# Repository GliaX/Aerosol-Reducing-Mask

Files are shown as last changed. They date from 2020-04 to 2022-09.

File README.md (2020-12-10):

November 27, 2020

# Suspension of Marketing and Sales of the Aerosol-Reducing-Mask (ARM)

Effective November 27 (2020), the ARM team is suspending any sales or distribution of the current version of the ARM.

Review of clinical trial data that became available to the team on November 26  shows that the ARM device is not as effective at reducing leak and aerosolization as earlier data had suggested. The [preliminary data and analysis report](https://github.com/GliaX/Aerosol-Reducing-Mask/blob/master/reports/20201210%20Clinical%20Trial%20Summary%20Leak%20Data.md) is posted to the repository.

The clinical trial was not a requirement for regulatory approval from Health Canada and the device is still approved under an Interim Order. However the trial data suggests that while safe and effective at providing respiratory support, the device fails to meets its primary indication (protection of health care providers and other patients from infectious aerosols), we are withholding all sales and deployments of the device.

We are currently undertaking a detailed analysis of the device and causes of failure in order to create a road map for required modifications for a subsequent version. Such modifications and the necessary testing will likely not be completed in sufficient time to meet current urgent needs. All analysis reports and other documents will continue to be posted on the public repository.

# Aerosol Reducing Mask for Non-Invasive Ventilation

## Purpose
The Minimizing Aerosolization In Non-invasive (MAIN) Ventilation COVID-19 mask
is a sealed, filtered, full-face mask minimizing virus aerosolization and
enabling the use of Non-Invasive Positive Pressure Ventilation (NIPPV) machines
for patients with COVID-19, or similar symptoms.  The mask adaptor is the
primary connection between the sealed facemask and standard medical 22mm
respiratory tubing, fittings and filters. An additive manufacturing method, also
known as 3D printing, was used to produce the mask adapter because of its
relative speed to make objects of complicated geometries and availability. Due
to the medical nature of the adapter, certain specifications must be followed in
its production to prevent any infectious transmission from the patient to health
care workers and other patients.

## Bill Of Materials
 * [3M Scott AV-2000 Facepiece](https://www.3mscott.com/products/av-2000-facepiece/)
 * 3M Gasket seal
 * 3D printed adapter (ABS)
 * Safety release strap, 25mm width x 35cm length[[MEC](https://www.mec.ca/en/product/5020-829/1%22%2825mm%29-Nylon-Tubular-Climbing-Webbing)]

## Adaptor 3D Printing Specifications and Parameters

 * Adapter Version: v1.0
 * Filament Material: ABS
 * Printer Nozzle: 0.4mm
 * Infill Percentage & Pattern: 100% Infill, Rectilinear infill
 * Wall thickness: 2.0mm (5 wall/perimeters with 0.4mm nozzle)
 * Top and bottom thickness: 2.0mm (5 top and bottom layers at 0.2mm layer height)
 * Supports: Required
 * Raft: Not preferred; Printing on the bed creates a smoother finish
 * Orientation: Mask face on the bed, Outer face upwards (See Figure 1)

Additional Slicer Settings:
 * Use ‘random start points for all perimeters’ (Cura)
 * Use ‘Connect infill lines’ (Cura)
 * Use ‘Random start points for all perimeters’ (Simply3D)

Figure 1: Orientation of Adapter v1.0 on Print Bed

*Figure 1: Orientation of Adapter v1.0 on Print Bed*

* NOTE: ABS is prone to thermoplastic contraction (shrinkage). If the slicing
software does not already compensate for this shrinkage, consider measuring the
product to ensure the correct scale. Amount of contraction can vary between
different brands of ABS – printing calibration tools and test-prints recommended
to determine exact percentage to scale.

## Post-Print Check Guidelines
Ensure the following:
 * Inside diameter of female port on outward face should measure between 22.37
 +0.1/-0.15mm on outside face (see Figure 2). Use of digital calipers strongly
 recommended.
 * Note tolerances for other dimensions post printing (also see Figure 2).
 * Layers adhere properly to each other
 * Walls are completely fused together
 * Surfaces (outer and inner) are smooth without gaps, burrs, blobs
 * The print has decent flexibility (i.e. latch)

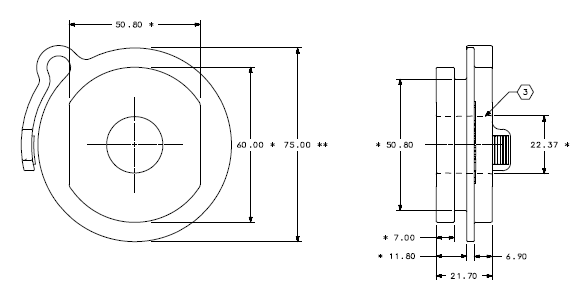
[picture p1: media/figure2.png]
Figure 2: Critical part dimensions


*Figure 2: Critical part dimensions*

# Print Traceability Guidelines

For each batch printed, the following items must be logged:
 * Material used
 * Lot number of material used
 * Colour of material
 * Date of print
 * Machines used for print
 
# Attaching safety release
 
 * Insert strap into bottom right buckle of helmet - Patient should be able to pull strap with right hand.
 * Loop strap back approximately 6 cm.
 * Sew firmly using 3 runs across the area to sew.
 
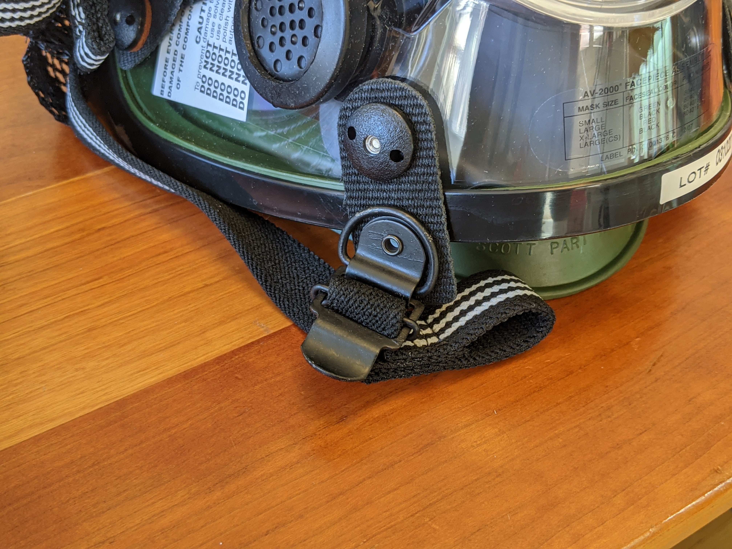
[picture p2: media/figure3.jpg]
Figure 3: Front view of helmet

 
*Figure 3: Front view of helmet*
 
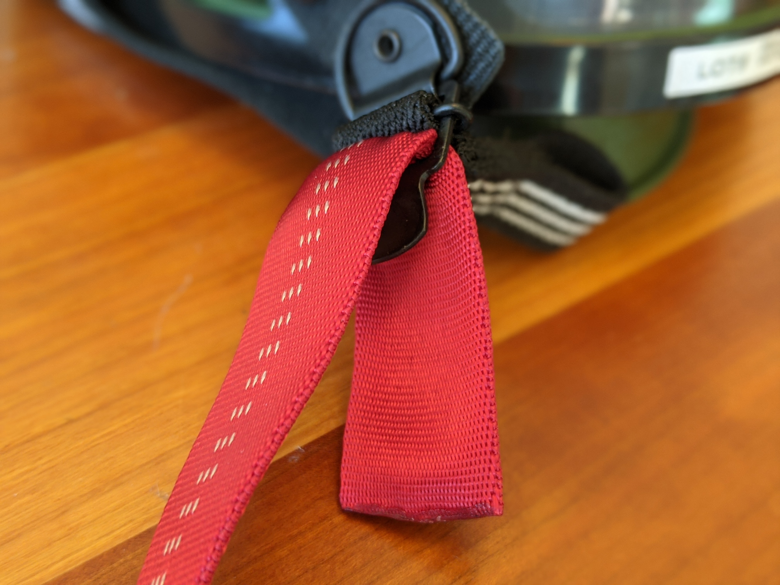
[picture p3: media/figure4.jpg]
Figure 4: Strap inserted into buckle


*Figure 4: Strap inserted into buckle*

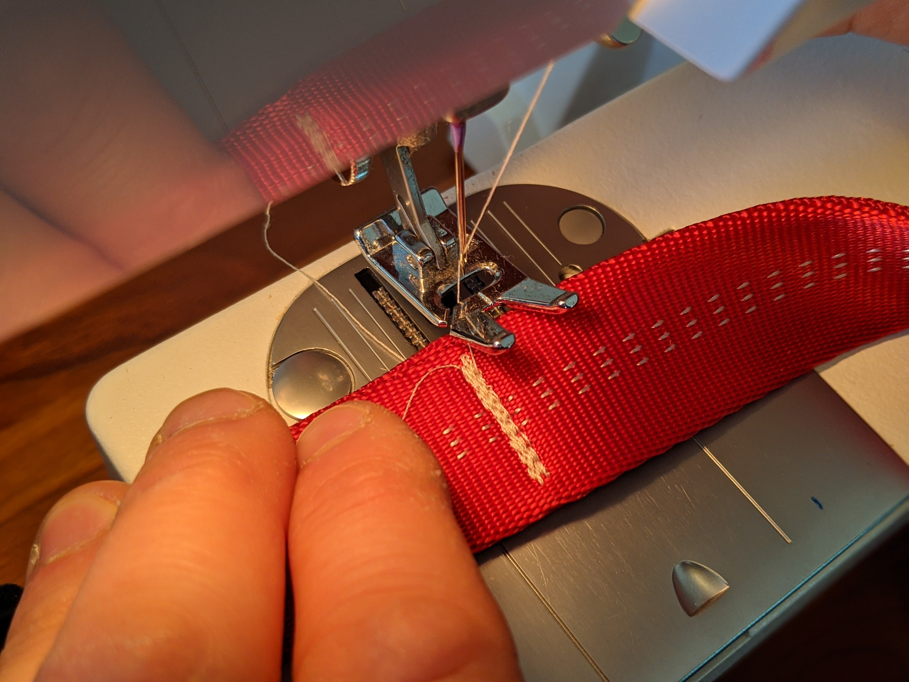
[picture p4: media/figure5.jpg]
Figure 5: Completed sewn strap

 
*Figure 5: Completed sewn strap*

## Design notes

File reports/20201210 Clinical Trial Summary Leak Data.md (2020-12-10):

---
tags: Glia-ARM
---
# Glia-ARM Clinical Trial Summary Report of Leak Data

Source: https://hackmd.io/@ARM/HyMZ32JnP

## Objective
To evaluate the effective leakage of the ARM compared to current standard of care NIV masks in patients undergoing emergent CPAP or BiPAP treatment.

## Methods
<small>The study was an opportunistic randomized controlled trial.

After [HSREB approval at Western University](https://github.com/GliaX/Aerosol-Reducing-Mask/blob/master/ethics_application/2020-04-27%20Ethics%20Approval.pdf) participants determined to require non-invasive ventilation by attending MDs in the emergency departments of affiliated teaching hospitals were recruited and randomized to the ARM or control standard mask ([Fisher & Paykel RT043M non-vented mask with anti-asphyxiation valve](https://www.fphcare.com/en-ca/hospital/adult-respiratory/noninvasive-ventilation/rt043/)).

Patients requiring NIV for an actue indications were assessed for inclusion. Exclusion criteria were: Age $\lt$ 18 years; respiratory failure due to non-pulmonary pathology; impaired level of consciousness (Glasgow coma scale $\lt$ 10); upper gastrointestinal bleeding; Chest trauma; Agitatation or violence.

Patients were ventialted using a Resmed (San Diego, US) Stellar 150 Non-invasive ventilator. The device's internal leak logging system was used to document mask leak. Trial was continued until either NIV was no longer deemed medically indicated by the attending team to a maximum of 24 hours. Arterial or venous blood gases collected during routine care of the patient were monitored to ensure adequacy of ventilation.

Primary end-point was proportion of time under treatment with mask leak $\lt$ 0.5 L/min (registering as 0 L/min by machine). Secondary end-points included ulceration score (National Advisory Panel on Pressure Ulcer Scale), mask fit (Likert-like 5 point scale, 1 = poor; 5 = excellent); and patient tolerance of the device (1 = poor; 5 = excellent).

Additional collected data included: demographics (age, sex); morphologic parameters (height, weight, presence of dentures, facial hair); metabolic data (arterial or venous blood gas); vital signs (temperature, pulse, respirations, blood pressure, oxygen saturation); Ventilation parameters (mode, IPAP, EPAP) and fit and comfort (mask fit evaluated by RT, and patient tolerance of mask).

</small>

## Results
The study was stopped after randomization of 16 patient (6 intervention, 10 control) due to results suggesting failure of the ARM to reduce leaks compared to the control device (Fig T1 & T2).

There were no major adverse events during the trial related to the device. 

T1. Mask Leak - Control

***Fig T1**. Distribution of mask leak flows for each patient with the control mask (N=10). 7/10 patients had leak of 0.5 L/min or less for at least half of the treatment duration*

T2. Mask Leak - ARM

***Fig T2**. Distribution of mask leak flows or each patient with the ARM (N=6). Only 2 of 6 patients had leaks of 0.5 L/min or less for more than half of the treatment duration*.

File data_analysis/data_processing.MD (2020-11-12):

* Download and compile [EDF2ASCII](https://www.teuniz.net/edf2ascii/)
* Get data from patient
* Start time is found in 

```
for f in `ls *BBB.edf`; do ~/workspace/EDF/edf2ascii $f; cat ${f%%.*}_annotations.txt | grep -i leak > ${f%%.*}_leak.txt; sed -i 's/,Leak://g' ${f%%.*}_leak.txt ; done

```

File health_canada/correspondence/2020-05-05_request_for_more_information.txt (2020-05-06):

Dear Dorotea and Dr. Loubani:

This pertains to the interim order application for the above device.  We require the following information to complete our assessment: 

1)     Since some components are 3D printed, provide biocompatibility testing results for any identified risks as per ISO 18562-1 and 10993-1.
2)     Can you comment on what the impact on patients sleep and ability to communicate, or to remove the mask without assistance?
3)     Are there any issues with rebreathing carbon dioxide?
4)     Where is the expired breath vented to following the HEPA filters shown in your picture provided for the setup.

Please contact me if you have additional questions.

Sincerely,

Melinda

Melinda Ché
Health Canada | Santé Canada
Medical Devices Directorate | Direction des instruments médicaux

Director General’s Office | Bureau du directeur général
Email |Courriel melinda.che@canada.ca
Telephone | Téléphone 613-941-1143 / Facsimile | Télécopieur 613-957-9969
Government of Canada | Gouvernement du Canada

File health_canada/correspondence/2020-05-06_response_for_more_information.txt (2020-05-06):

Hello Ms. Ché and Mr. Nguyen,

Thank you for your email and questions. All figures referred to below
can be found at https://cloud.emlondon.ca/s/oiPjpx6kogXR66P .

1. I have inserted the correct address for Dr. Gucciardo. glia.com is a
different entity.

2. Regarding biocompatibility, the item that is 3D printed is the
adapter between the mask and the non-invasive ventilation (aka Adapter).
The material we are utilizing is Acrylonitrile Butadiene Styrene,
commonly known as ABS. This is the material that is used in Lego, for
example.

We reviewed ISO 10993-1. This ISO applies to the 3M AV2000 mask we use,
which is in wide and common use. Any information about this mask will be
provided to you upon request. ISO 10993-1 does not appear to directly
apply to the 3M gasket and 3D printed adapter.

Section 3.11 puts our adapter (and overall device) within the scope of
10993-1 by considering it a medical device with direct (3M AV2000 mask)
and indirect contact (Adapter and Gasket).

However, 5.1 redirects us to 18562 (1-4) for gas pathway devices, which
applies to the 3D printed adapter and 3M gasket.

Of note, we reviewed ISOs 10993-4 and 10993-5 and found that they do not
apply to this device. We also reviewed ISOs 18190, 80601-2 (79, 80), and
17510 and have incorporated them into the development of this device.

As per Figure 1 of ISO 18562-1, our risk assessment identified two areas
of concern:

2.a. The printing process and subsequent i) biocontamination and ii)
porosity of the device

2.a.i) Regarding biocontamination, we concluded that data exist and
reviewed the whitepaper entitled "Sterilization of FDM-Manufactured
Parts" [1] by Stratasys, the world's foremost manufacturer of 3D
printers and 3D printed medical equipment. This study concluded that
"based on the results obtained in this paper, it
 appears that each of the four methods tested are
 successful in sterilizing these materials." Concerns were raised with
one of the methods (autoclave heating) regarding ABS's integrity.
However, the other three methods achieved full sterilization.

2.a.ii) Regarding porosity, we concluded that data do not exist. We
created a test rig in the laboratory and tested the device for porosity
using various print settings. Figures 1a-c (see link above) show photos
of the test set up in which pressurized air far exceeding operating
standards was put through the device to test porosity. No porosity was
found in the adapter at pressures up to and far exceeding operating
pressures.

2.b. The ABS being used as a material.

ABS is a commonly used material in all parts of food, drug, and medical
device industry that is well-accepted as being biocompatible. Our
evaluation plan concluded that data exist for its biocompatibility. We
reviewed several resources [2-6] and the MSDS[7], and concluded that ABS
is a safe, biocompatible and inert material for gas exchange. It is
vulnerable to solvents such as acetone which are not expected to be used
in a hospital environment. It is otherwise inert. It is compatible with
common cleaning methodologies in hospitals such as gluteraldehyde, vapor
phase hydrogen peroxide and 1-minute bleach bath.

3. Regarding the patient's ability to sleep and communicate, clearly
these are impeded by the use of any mask. However, this mask should not
impede the ability of patients to sleep or communicate more than other
masks. We have already begun clinical trials on this mask, and patients
are comprehensible while wearing the mask and are easy to assess for
clinical status and concern.

Regarding the patient's ability to remove the mask without assistance,
the device contains a release strap that will quickly release the mask
from a patient's face. The colour of this strap is bright red. I have
attached video of the release mechanism as Figure 2 (see link above).
Please note that in this engineering demonstration, the strap is black
in colour whereas on the product it is bright red.

4. Regarding the rebreathing of carbon dioxide, the device has two
configurations: single limb and dual limb ventilation. In a single limb
setup, the device must be attached to an exhalation port and an
anti-asphyxiation valve within the circuit. The combined exhalation port
anti-asphyxiation valve being used is the "ResMed 24991 Leak Valve". An
example single limb setup would be with a ResMed Stellar noninvasive
ventilator machine.

In a dual limb setup, the second limb provides the exhaust and
anti-asphyxiation capability routinely and without any additional valves
or ports. An example dual limb setup would be the Hamilton Medical C1.

5. Regarding the expired breath following filtration by a viral filter,
it is expired to the room, as it is considered decontaminated by the
viral filter. This is the routine method used by all non-invasive
ventilators.

I hope this answers all of your questions. Please do not hesitate to
raise any further questions.

Thank you,

Tarek : )

----
Tarek Loubani, BSc(Hon), MD, CCFP (EM)
Consultant, Department of Emergency medicine
London Health Sciences Centre

Associate Professor, Department of Medicine
Faculty of Medicine and Dentistry
University of Western Ontario

Medical Director
Glia

References:

1.
http://www.stratasys.com/-/media/files/white-papers-new/wp_fdm_sterilization_en_0915-web.pdf

2.
https://www.hcltech.com/sites/default/files/an_overview_of_the_plastic_material_selection_process_for_medical_devices.pdf

3.
https://omnexus.specialchem.com/selection-guide/acrylonitrile-butadiene-styrene-abs-plastic

4. https://www.ensingerplastics.com/en-us/shapes/biocompatible-medical-grade

5. https://amfg.ai/2018/06/29/abs-plastic-3d-printing-all-you-need-to-know/

6.
https://3dprintingcenter.net/2020/03/29/spectrum-filaments-introduces-medical-materials-to-the-offer-including-biocompatible-abs/

7. https://www.tapplastics.com/uploads/pdf/MSDS%20ABS.pdf

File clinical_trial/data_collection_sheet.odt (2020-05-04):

Data Collection Sheet

Study information

Collecting researcher: Date: 2020 / /

Patient ID: Patient PIN:

Machine Type: Machine #:

Study initiation time:

Consent signed? Y N

Was consent delayed? Y N

If Yes, reason:

Randomization Group: Control Experimental

Demographic information

Gender: M F non-binary

Age:

Height:

Weight:

Does patient wear dentures? Y N

Does patient have facial hair? None Moustache Short beard Full beard Other

COVID status: Confirmed Pending Negative

Metabolic Data

| 0 hours | 4 hours | 12 hours | 24 hours
Glasgow Coma Scale (refer below)
Respiratory rate
Heart rate
pH
HCO3
PaCO2
PaO2
SpO2

Non-invasive ventilation data

| 0 hours | 4 hours | 12 hours | 24 hours
Ventilation technique (BiPAP, CPAP)
IPAP
EPAP
Mask fit (1-5 scale, 1 = poor; 5 = excellent) *If not excellent, state reason.
Patient tolerance of BiPAP mask (1-5 scale; 1 = poor; 5 = excellent)

Adverse events data

| 0 hours | 4 hours | 12 hours | 24 hours
Ulcer staging on face (refer below)
Nasal or oral bleeding
Pneumothorax
Other concerns

Outcome at 24 hours: Intubated Still on NIV Discontinued from NIV Deceased

Total NIV time (hours):

Explain outcome above:

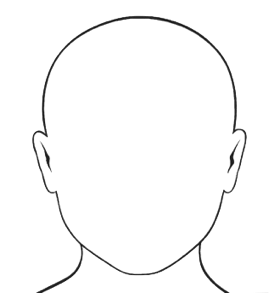
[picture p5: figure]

Disposition: If ulcer, indicate location:

Glasgow Coma Scale

Domain | Response | Score
Eye Opening | Spontaneous | 4
| To speech | 3
| To pain | 2
| None | 1
Best Verbal Response | Oriented | 5
| Confused | 4
| Inappropriate | 3
| Incomprehensible | 2
| None | 1
Best Motor Response | Obeying | 6
| Localizing | 5
| Withdrawal | 4
| Flexing | 3
| Extending | 2
| None | 1

Ulcer Score (NPUAP Staging System for Pressure Ulcers)

Stage | | Description
0 | n/a | No ulcer

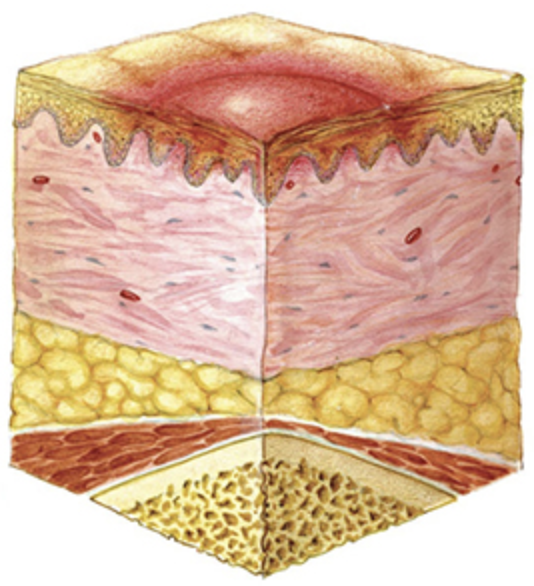
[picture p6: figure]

I | | Intact skin with non-blanching redness.

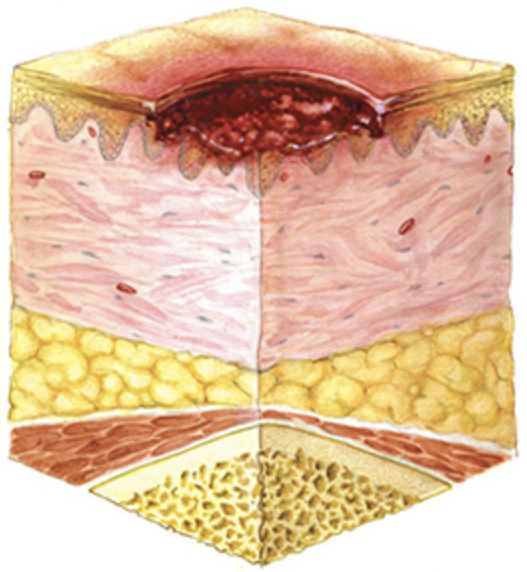
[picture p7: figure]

II | | Partial-thickness loss of skin or tissue presenting as a shallow open ulcer with a red-pink wound bed, without slough.

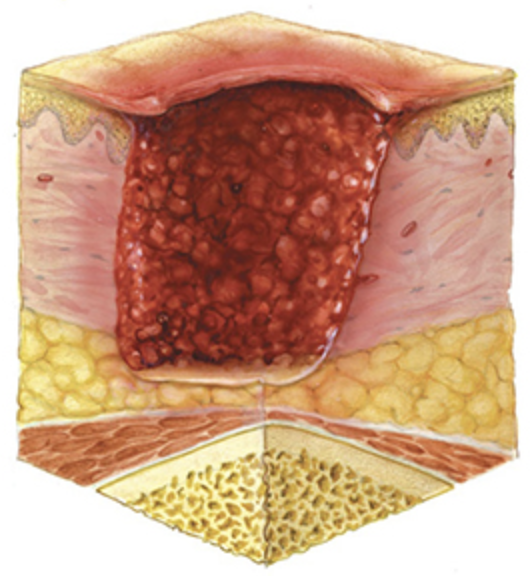
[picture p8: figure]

III | | Full-thickness skin loss; subcutaneous fat may be visible, but bone, tendon, or muscle is not exposed; slough may be present but does not obscure the depth of tissue loss; may include undermining and tunneling.

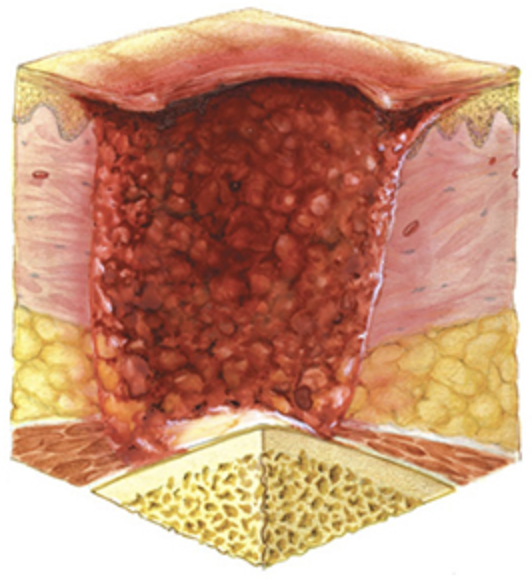
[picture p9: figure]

IV | | Full-thickness tissue loss with exposed bone, tendon, or muscle; slough or eschar may be present; often includes undermining and tunneling.

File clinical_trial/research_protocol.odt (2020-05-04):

800 Commissioners Rd East • London, Ontario • N6A 5W9 • Canada Telephone: (519) 685-8500 ext 76089 • Fax: (519) 667-6769Division of Emergency Medicine

# Non-invasive positive pressure ventilation mask to minimize mask leak and potential aerosolization leading to spread of virus such as COVID-19

## Research Protocol

Principal Investigator: Dr. Tarek Loubani

Co- Investigators: Dr. Scott Anderson

BACKGROUND AND SIGNIFICANCE

Patients presenting to emergency departments and hospitals for various medical conditions often require non-invasive ventilation (breathing support). For example, a person with shortness of breath as a complication of COPD (chronic obstructive pulmonary disease) may be treated with a BiPAP machine, one type of non-invasive ventilation.

However, in the current environment of COVID-19, aerosols produced by a BiPAP machine in a COVID-19 positive patient pose serious potential harms to healthcare providers and other patients. All patients with similar symptoms to COVID-19 are presently treated as positive until definitive testing determines otherwise. The best test available for COVID-19 takes up to 4 hours to determine the patient's status, which is too long to delay application of BiPAP in a distressed patient. This could lead to either a delay in care or the need for invasive breathing measures (intubation), which requires intense resource utilization, may not be in line with a patient's goals of care, and could cause serious harms (i.e. infection, medication reactions, etc.) in patients who do not need it.

As well, the lack of BiPAP as an option in the clinician's arsenal leads to increased ventilator days that would previously have been bridged with a BiPAP machine. The use of a closed-loop BiPAP machine in which no expired air is released into the environment would solve these problems. Building off the experiences of a similar approach that was trialed in Italy in response to the COVID-19 crisis, this project will develop and test a novel BiPAP mask that reduces mask leaks and thus aerosolization.

Few studies have been done on the potential harm caused by aerosolization from non-invasive ventilation¹. The data available suggest that caution must be taken with acute respiratory infection (ARI) patients when placing them on non-invasive ventilation such as CPAP or BiPAP due to excess risk to health care workers¹⁻⁴. This advice is being heterogeneously applied during the recent COVID-19 pandemic, with some practitioners advocating the use of non-invasive ventilation⁵.

There is a role for non-invasive ventilation in COVID-19 negative patients during the pandemic, although practitioners are reluctant to initiate these measures because of the slow speed, lack of reliability and lack of availability of the viral swab confirming corona virus status. This study seeks to ensure that an easy-to-produce, specifically engineered mask and circuit has the ability to maintain non-invasive ventilatory support without aerosolizing viral particles. If successful, this will return an important tool to the clinician’s arsenal.

Dr. Tarek Loubani has a history of success in the development and validation of high-quality, low cost medical devices that are manufactured and made publicly available through the Glia Project, a non-profit organization solely owned by Dr. Loubani. He has received several notable awards for his work including the Shuttleworth Foundation and Bassel Khartabil Fellowships.

Dr. Tarek Loubani has worked with the Division of Emergency Medicine, London Health Sciences, Inštitut za Razvoj Naprednih Aplikativnih Sistemov (IRNAS), Glia and others to bring to market the 3D printed Glia stethoscope, tourniquet and otoscope. Additionally, there are ongoing trials to validate and calibrate a 3D printed pulse-oximeter and electrocardiograms.

The need for a reduced-aerosolizing non-invasive ventilation mask was made apparent with the current pandemic. Dr. Loubani and a team of physicians spanning relevant specialties (emergency, anesthesia, internal medicine and critical care) across several hospital regions in Ontario (London, Toronto, Kingston) provide insight into device design. This work is a collaboration between the Division of Emergency Medicine, London Health Sciences (LHSC), Glia, Toronto General Hospital Advanced Perioperative Imaging Lab (TGH-APIL), University Health Network (UHN), McKenzie Health, and General Dynamics Land Systems (GDLS).

The Division of Emergency Medicine provides research support to this study. LHSC provides support in execution of this study. Glia provides logistical, Health Canada, open source development and 3D printing support. TGH-APIL provides device development and research support. McKenzie Health provides device development and research support. GDLS provides initial prototype design and laboratory testing to demonstrate the fit of the mask with reduced air leaks, adequate air flow, and ease of connection to ventilators.

Proof of this concept has occurred in the laboratory and clinical validation is being pursued.

STUDY OBJECTIVE(S); INCLUDING SPECIFIC AIMS AND/OR HYPOTHESES

To validate that an easy-to-produce, specifically-engineered mask and circuit has the ability to maintain non-invasive ventilatory support while reducing aerosolization of viral particles

The primary objective of this study is to assess if the mask device leaks when attached to a patient's face in real-world use.

This outcome will be measured in two ways:

1. Through continuous recording of data from the ventilator (approximately every 3-10 seconds) of leak volume (L/min). This measurement is a normal output of modern ventilators.

2. Through interval checks of the seal by a respiratory therapist (RT), registered nurse (RN), or the most responsible physician (MRP).

The patient will be in a monitored care setting (as per standard of care for non-invasive ventilation) and will be monitored by a RN, RT, and the MRP in collaboration with the study team.

Monitoring will not deviate from the standard of care, as seal checks are routinely conducted and leak volumes are routinely displayed. The only change is that the data each machine collects will not be deleted, but will be exported for use in this study.

Participants will be enrolled in the study for up to 24 hours of their BiPAP treatment after entering the study.

The secondary objective of the study is to assess markers of ventilation and perfusion in patients, including pH, pCO2, pO2, respiratory rate, heart rate and level of consciousness (via GCS).

These markers will be measured through routine vital signs monitoring (respiratory rate, heart rate and GCS) and an arterial or venous blood gas (pH, pCO2, pO2).

METHODS

Study Design

This study is an opportunistic prospective randomized controlled trial.

If experimental non-invasive ventilation masks are available in the patient's expected size, patients will be randomized to control masks or experimental. If experimental masks are not available, the patient will be consented and entered into the control arm. Patients who receive BiPAP or CPAP with the mask are assessed for several variables over time to ensure adequate treatment and assess leaks.

Study Population

The study population will include patients in the Emergency Department or an in-patient in a monitored or ICU setting requiring non-invasive ventilation for respiratory distress or hypercapnia at both London Health Sciences Centre. This population will include both the Victoria Hospital site and University Hospital site. The local sample size is n=50.

Inclusion Criteria:

- Patient with respiratory failure due to primary pulmonary pathology.
- Patient who is selected for BiPAP or CPAP by the health care provider

Exclusion Criteria:

- Age <18 years.
- Respiratory failure due to non-pulmonary pathology.
- Impaired consciousness (Glasgow coma scale <10).
- Patients with contraindications of NIV.
- Severe upper gastrointestinal bleeding.
- Chest trauma.
- Agitated or violent patient.

Study Procedures

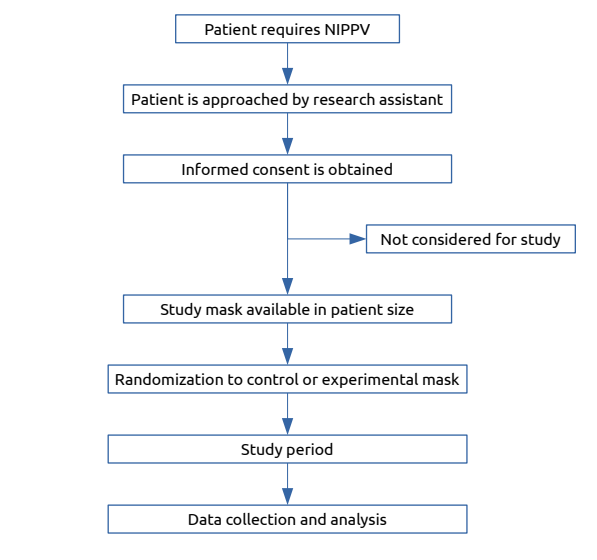
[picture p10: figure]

A patient may be enrolled in this study if they require BiPAP in the following circumstances:

1. Immediately on arrival to the emergency department

If a patient arrives to the emergency department through the waiting room or via ambulance, an emergency department MD will assess the patient to determine the most appropriate care. If non-invasive ventilation is the most appropriate course of action for this patient and they are unable to provide consent due to their current respiratory status, the SDM may provide consent or consent will be delayed until the SDM is available or the patient is able. There will be no delay in care in order to obtain consent.

The patient will be immediately taken to the designated negative pressure care area. The assigned registered nurse (RN), medical doctor {MD), and respiratory therapist (RT) will doff enhanced PPE and the patient will be hooked up to BiPAP using the MAIN Covid Mask.

The patient will be monitored closely by the assigned RN, RT, and MD. The health care team will immediately ensure that the patient is tolerating the mask and that their respiratory status is improving. This can immediately be observed by the patient’s oxygen saturation level (Sp02) and respiratory rate. This patient would be hooked up to a cardiac monitor with continuous oxygen monitoring to ensure continued efficacy and no decline of the patient’s condition.

If the patient decompensates or the device is proving to have significant air leaks, the patient will be switched to the appropriate support (e.g. intubation) based on the judgement of the most responsible physician (MRP).

2. At any time throughout their visit in the emergency department

If a patient arrives to the emergency department through the waiting room or via ambulance and the patient does not immediately require ventilatory support, the patient will be triaged and assessed according to their condition. If the patient has respiratory complaints, the physician will discuss the patient’s goals of care. If noninvasive ventilation is part of the goals of care and appears imminent, consent for the study treatment will be obtained for future use if the patient condition worsens, indicating the need for non-invasive ventilation.

3. At any time during their hospital admission

When a patient is admitted to the hospital, the admitting consultant or resident discusses the patient’s goal of care and code status. At this time, if the patient agrees to non-invasive ventilation and its use appears imminent, consent may be obtained should the patient’s condition worsen and require non-invasive ventilation.

The direct measurement of aerosols is non-trivial. However, aerosols travel in air, and so air leak is a necessary condition for aerosolization. This study measures air leaking around a mask as approximated by air leaking out of a circuit as an indirect measurement of aerosolization.

DATA COLLECTION

Demographic Data: age, sex, height, weight, presence or absence of dentures, presence or absence of facial hair

Metabolic Data: arterial or venous blood gas measurements (pC02, pH, HC03, and p02), vital signs (body temperature, pulse, respirations, blood pressure, oxygen saturation).

Note: no additional blood work beyond standard patient care will be required for the study.

Non-invasive Ventilation Data: Ventilation technique, IPAP, EPAP, leak volume per minute, mask fit, patient tolerance of mask.

Adverse events Data: From initiation to completion of non-invasive ventilation using the standard or non-aerosolizing mask, any reports of : nasal or oral bleeding, pneumothorax, ulcers, and free text for other concerns.

Note: The electronic medical record (Power chart) will be accessed to review this data

All data will be tracked by the DSMC to ensure safety of patients. Where possible, the committee will analyze data to ensure patients are ventilating as expected by compiling and reviewing all bloodwork results found in the blood gases.

DATA ANALYSIS

Data will be entered directly into a study-specific LibreOffice database (The Document Foundation, Berlin, Germany). All data analyses will be performed using R (R Foundation, Vienna, Austria). All identifying patient data will be kept separate from study data. LibreOffice and R are two pieces of Open Source software that will be run locally on study computers and store all data to the LHSC P: drive. A LibreOffice database is stored in an ODS (Open Document Spreadsheet) file. It is a storage format akin to Microsoft Excel's XLSX format. LibreOffice Calc is the software used to create the database, and is an Open Source Software (OSS) equivalent of Microsoft Excel.

Data from the BiPAP machine (IPAP, EPAP, L/min of leak) are collected nearly continuously (every 3-10 seconds depending on machine) on the ResMED 150 or similar machine. An alarm will sound on the machine if leak volume exceeds standard of care. The leak volume will be reviewed with data analysis after the duration of BiPAP or at 24 hours. Data will be transferred from this machine to a local computer for entry into the above database.

For Data Analysis, the means and standard deviations of the Glasgow coma scale (GCS), respiratory rate, heart rate, pH, PaCO2, and PaO2 will be calculated for each time period.

Participants will be assigned a subgroup of control or experimental depending on which mask the patient received. These two subgroups will be compared using an analysis of variance (ANOVA) to detect differences between outcome parameters. A subgroup analysis will also be taken based on COVID-19 culture status regardless of the type of respiratory failure. This analysis will be performed with an ANOVA on the outcome parameters.

The critical importance of mask leaking means that these data will be displayed as a sum of all incidents. As these are binomial, a subgroup and time comparison will also be carried out using a generalized linear model of the binomial family (logistic regression). Leak volumes will be compared with an ANOVA.

As there is a real or perceived conflict of interest, Dr. Tarek Loubani will not be involved in any data analysis.

ETHICS AND PRIVACY

The research team will seek approval from Western Health Sciences Research Ethics Board.

All data collected will be maintained on the LHSC “P” Drive in a password protected folder. Investigators will only look at or analyze data on LHSC computers. Hard copies will be stored in a locked filing cabinet in a secured location. Data will be coded with unique identifiers and the master list containing any identifiers will be stored separately from the collected data.

There will be no additional information stored on any external hard drives, laptops, or portable devices.

This study data will be retained for 15 years as per Health Canada policy. After this 25 year period, paper records secured in a locked filing cabinet at LHSC will be destroyed according to institutional protocols, which includes placing the records in locked, confidential shredding bins. The bins are then collected by an outsourced company (Shred-It) and the contents are shredded. Computer and electronic records will be encrypted and secured for 25 years and then all study files will be destroyed according to institutional protocols of data deletion including clearing all memory sticks. This will be done in consultation with the IT department for current protocols.

PLANS FOR DISSEMINATION OF FINDINGS

The source code for the device, anonymized data from the study, and preprints will be stored in a local repository and submitted for publication.

The investigators will also disseminate findings through mass media and peer-reviewed publication.

References

1. Tran K, Cimon K, Severn M, Pessoa-Silva CL, Conly J. Aerosol Generating Procedures and Risk of Transmission of Acute Respiratory Infections to Healthcare Workers: A Systematic Review. PLOS ONE. Public Library of Science; 2012 Apr 26;7(4):e35797.

2. American Journal of Respiratory and Critical Care Medicine [Internet]. [cited 2020 Apr 1]. Available from: https://www-atsjournals-org.proxy1.lib.uwo.ca/journal/ajrccm

3. Raboud J, Shigayeva A, McGeer A, Bontovics E, Chapman M, Gravel D, Henry B, Lapinsky S, Loeb M, McDonald LC, Ofner M, Paton S, Reynolds D, Scales D, Shen S, Simor A, Stewart T, Vearncombe M, Zoutman D, Green K. Risk Factors for SARS Transmission from Patients Requiring Intubation: A Multicentre Investigation in Toronto, Canada. Montgomery JM, editor. PLoS ONE. 2010 May 19;5(5):e10717.

4. Guan L, Zhou L, Zhang J, Peng W, Chen R. More awareness is needed for severe acute respiratory syndrome coronavirus 2019 transmission through exhaled air during non-invasive respiratory support: experience from China. Eur Respir J [Internet]. European Respiratory Society; 2020 Mar 1 [cited 2020 Apr 1];55(3). Available from: https://erj-ersjournals-com.proxy1.lib.uwo.ca/content/55/3/2000352 PMID: 32198275

5. Pulmonary SMF is the creator of P org H is an associate professor of, Vermont CCM at the U of. PulmCrit Wee- Could the best mode of noninvasive support for COVID-19 be… CPAP ?? [Internet]. EMCrit Project. 2020 [cited 2020 Apr 1]. Available from: https://emcrit.org/pulmcrit/cpap-covid/

Version Date: 2020 April 22

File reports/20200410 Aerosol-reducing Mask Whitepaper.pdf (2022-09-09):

## Non-invasive positive pressure ventilation mask to minimize mask leak and potential aerosolization leading to spread of virus such as COVID-19

## Engineering Team:

Wes Rhiger ¹

, Bethany Brasser ¹

, Derek Wilson¹

, Kipp ???? ¹

, Lawrence
Nugent ¹

, Nick Edwards ¹

, Ray Szeto¹

, Tyler Finlayson¹

## Medical Team:

Benjamin Thomson²

, Azad Mashari ³

, Scott Anderson ⁴

, Tarek Loubani ⁴

1General Dynamics Land Systems Canada, London, Ontario 2Mackenzie Health, Richmond Hill, Ontario
3Toronto General Hospital, Toronto, Ontario

4
London Health Sciences Centre, London, Ontario

aerosol-reducing mask

### Background

A major challenge associated with Coronavirus Disease (COVID-19) is the demand it places on the use of invasive ventilators. Traditional non-invasive ventilation strategies, such as Continuous Positive Airway Pressure (CPAP) and Bi-level Positive Airway Pressure (BiPAP) vent directly to the atmosphere due to masks that are not fully sealed.
Few studies have been done on the potential harm caused by aerosolization from noninvasive ventilation. The data available suggest that caution must be taken with acute respiratory infection (ARI) patients when placing them on non-invasive ventilation such as CPAP or BiPAP due to excess risk to health care workers. This advice is being heterogeneously applied during the recent COVID-19 pandemic, with some practitioners advocating the use of non-invasive ventilation. The American Society of Anesthesiology presents some typical advice:
“In patients with acute respiratory failure, it may be prudent to proceed directly to endotracheal intubation, because non-invasive ventilation (e.g. CPAP or BiPAP) may increase the risk of infectious transmission.”

There is a role for non-invasive ventilation in COVID-19 negative patients during the pandemic, although practitioners are reluctant to initiate these measures because of the slow speed, lack of reliability and lack of availability of the viral swab confirming corona virus status.
The lack of non-invasive ventilation as an option in the clinician's arsenal leads to increased ventilator days that would previously have been bridged with non-invasive machines. The use of a closed-loop BiPAP machine in which no expired air is released into the environment would solve these problems.

### Objective

This project seeks to develop and validate a solution to allow the use of non-invasive positive pressure ventilation (NIPPV) machines for patients that have COVID-19, or similar symptoms. In order to be used against COVID 19, the solution must:
1. Drastically reduce risk of aerosolization of the COVID-19 virus
2. Provide sufficient sealing around the mouth and nose to maintain CPAP/BiPAP effectiveness
3. Filter patient exhaust with an N95 (or better) medical grade filter
4. Be easy to produce in resource constrained locations

The COVID-19 pandemic has spurred many developments in this area, from adapting full-face snorkel masks to placing patients in hyperbaric therapy helmets. Though somewhat effective, the sealing of the snorkel masks has been determined inferior and the masks, now popular, are in short supply. Hyperbaric helmets have also become in demand resulting in limited available supply of an uncommon medical device.

London Health Sciences Centre has predicted the number of local COVID-19 cases to reach a critical level by mid April, requiring approximately 100 mask solutions. Some models predict up to 5000 patients will require simultaneous non-invasive ventilation province wide shortly thereafter.
The medical team named the solution “MAIN COVID-19 Mask” (Minimizing Aerosolization in Non-invasive ventilation in COVID-19).

### Team Members

The engineering team from General Dynamics Land Systems is composed of 8 core contributors, and a number of part-time contributors, with a spectrum of expertise in administration, logistics, engineering, production, and distribution.
The medical team is composed of
- Dr. Ben Thompson – Medical Lead, Nephrologist at Mackenzie Health, and an Adjunct Professor at Queen’s University
- Dr. Azad Mashari – Department of Anesthesia and Pain Management, Toronto General Hospital, University Health Network; Assistant Professor at University of Toronto
- Dr. Tarek Loubani – Principal Investigator and Sponsor; and Medical Director for Glia. Glia provides Open Source medical supplies to resource constrained countries. Dr. Loubani is an Associate Professor at Western University

### Roles and Responsibilities

Engineering team
- Project Management, Engineering, Proof-of-Concept manufacture, Supply Chain Management

Medical team
- Medical expertise, patient safety. requirements definition, ethics and regulatory approvals, Application testing, grant applications

### Solution Use Cases

The proposed solution is intended for use in emergency rooms, intensive care units, prehospital transport, intra- and inter-hospital transport, and remote nursing stations. The following Use Case descriptions are provided to help illustrate the benefits of the MAIN COVID-19 Mask solution in real world situations.
This device will be used with:
1. Supplemental oxygen from flowmeter (either wall oxygen or oxygen concentrator).

2. Continuous Positive Airways Pressure (CPAP) and Bi-Level Positive Airway Pressure (BiPAP) non-invasive ventilator which has built in systems for controlling oxygen supplementation and managing and measuring pressures.
3. Either of 1 or 2, with nebulized medications

Use case 1: Remote Nursing Station:
“Bruce” is a 48 year old police officer who presents with breathing difficulty to the nursing station at Mishkeegogamang First Nation, a group of communities with a total population of 1500 approximately 250 km from Sioux Lookout where the nearest hospital is located. The nursing station is staffed by experienced nurses, with physician support available by telemedicine and intermittent visits by family physicians from Sioux Lookout.

The nursing station is equipped with a transport ventilator, 2 oxygen concentrators with maximum flow rates of 3LPM and 10LPM respectively. No Oxygen tanks are available. On assessment the nurse is concerned that Bruce’s oxygenation is deteriorating rapidly. He contacts the physician on call in Sioux Lookout who determines that Bruce will likely require intubation, mechanical ventilation and transfer to an intensive care unit in either Thunder Bay or Sudbury.

The on-call physician has to fly into the community to intubate the patient for transfer. An air ambulance is also scheduled, but both flights are delayed for several hours due to high demand in the Sioux Lookout Zone. Bruce is not able to maintain adequate Oxygen saturation on nasal prongs at 4 Liters per minute, and it may take 8-12hrs for the on-call physician to arrive.

Current Path: Due to concerns with aerosolization, Bruce cannot be placed on high flow nasal oxygen. Bruce remains on nasal prongs and nurses do best to keep him comfortable.

Proposed Path with MAIN COVID-19 Mask: Apply MAIN COVID-19 mask along with high-flow oxygen.

Use case 2: Patient presenting with shortness of breath to emergency room “Betty” is a 62 year old bank executive who comes to the emergency room triage desk with shortness of breath. Her vital signs (blood pressure, heart rate, respiratory rate, oxygenation status) are measured and her oxygen levels are low (85% on room air). Supplemental oxygen is provided by nasal prongs and Betty is placed in a room inside the main emergency room area.

She has blood tests, and is monitored every 15 minutes with vital signs and health care worker assessments. However, over the period of several hours, her oxygen requirements increase, and blood work confirms that she requires more than either standard or high flow nasal prongs can provide. The next step in providing additional respiratory support to Betty is non-invasive positive pressure ventilation (CPAP or BiPAP).

Current Path: Hospitals currently have a policy that patients presenting with symptoms consistent with COVID will not be offered NIPPV to prevent spread of the virus. Doctors must assume that anyone with symptoms comparable with COVID has the disease. Patients with COVID are often intubated for shortness of breath and connected to an invasive ventilator.

Proposed Path with MAIN COVID-19 Mask: With a device that reduces aerosolization of potential aerosol-borne viruses, health care workers will be able to administer the logical next step in providing additional respiratory support to Betty via NIPPV (CPAP or BiPAP). Betty may be on this treatment for anywhere from 2 hours to 5 days.

Use case 3: Intensive Care Unit with severe shortage of ventilators

Three weeks after the first case of COVID presented to a large academic hospital, all intensive care units, operating rooms and acute care areas in the hospital have been converted into ventilated wards. There is a severe shortage of ventilators with many patients sharing ventilators using experimental devices. Several patients with moderate but progressive hypoxic respiratory failure will likely require invasive ventilation in the next 24 hours. At the same time there are several ventilated patients who have largely recovered but still require low to moderate levels of positive pressure to adequately oxygenate.

Current Path: Doctors are forced to choose between which patients get invasive ventilation based on severity of symptoms and likelihood of recovery. These patients may not be COVID positive but due to the possibility of carrying the virus, and risk of aerosolization, they cannot be placed on NIPPV machines.

Proposed Path with MAIN COVID-19 Mask: Use the currently idle NIPPV machines along with MAIN COVID-19 Mask on low to moderate respiratory cases, and reserve invasive ventilators for more extreme cases.

### Accomplishments to Date

- Project kicked off March 28th
- Established requirements. See Appendix 1.
- Conducted an industry-wide search for all commercially available full face mask options (medical, chemical, scuba, oil & gas, firefighter). Decided on the use of 3M Scott Firefighter mask (AV2000 model) due to robustness of design, double sealing, and available stock.
- Selected the Medical DAR filter as it exceeds N95 filtering requirement, is in abundant supply within Hospitals, and is currently used in respiratory therapy systems.
- By leveraging 3D Printing, we conducted first Proof-of-Concept test within 48hrs of project kick-off and rapidly prototyped 6 iterations (in as many days) based on feedback from GDLS Engineers, medical team, and hands-on testing by Respiratory Therapists (RT). See Figure 1.

- Decided to limit 3D printing material options to ABS and PETG as both are commonly used already in medical equipment.

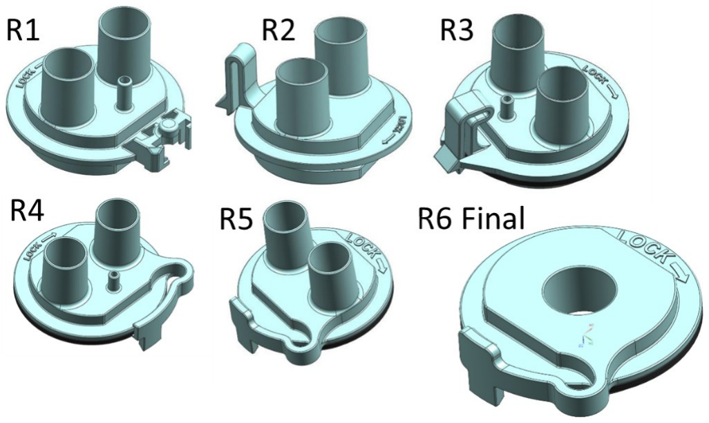
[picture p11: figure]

Figure 1 – ABS/PETG 3D Printed Adapter Versions

- Identified sources of supply, and received quotes for masks, gaskets, and 3D printed material.
- Conducted successful instrumented pressure and leak tests to operational limits.
- Also, conducted successful characterization testing to quantify impact of patient coughing. Performance was deemed acceptable. See Figures 2 through 4.
- Provided mask kit to medical team to conduct testing with RTs on Thursday, April 2nd .
- RTs successfully tested on different face sizes, machines, and circuit configurations with good results. Testing resulted in simplified circuit and adapter design. See Figure 5.
- Provided 4 prototypes to London Health Sciences Center (LHSC) on Saturday, April 4th .
Further protocol and process testing was successfully completed. LHSC leadership provided support to continue after witnessing testing.
- Completed porosity testing on 3DP printed adapters with 20%, 40%, 60%, 80%, and 100% infill. See Figure 6.
- Received first order of 100 masks on April 8th, placed follow on order for the remaining 900 masks.
- LHSC submitted Ethics Application which must be approved before clinical trials on patients.

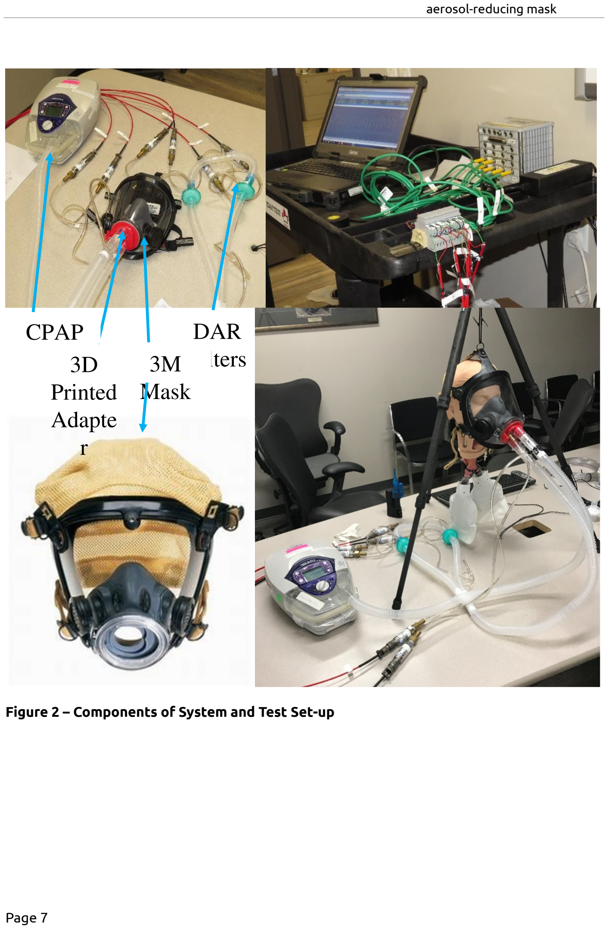
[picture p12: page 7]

Figure 2 – Components of System and Test Set-up

## DAR 3M Filters Mask

3D

## Printed Adapte r (https://www.bing.com/images/search?view=detailV2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)

## CPAP

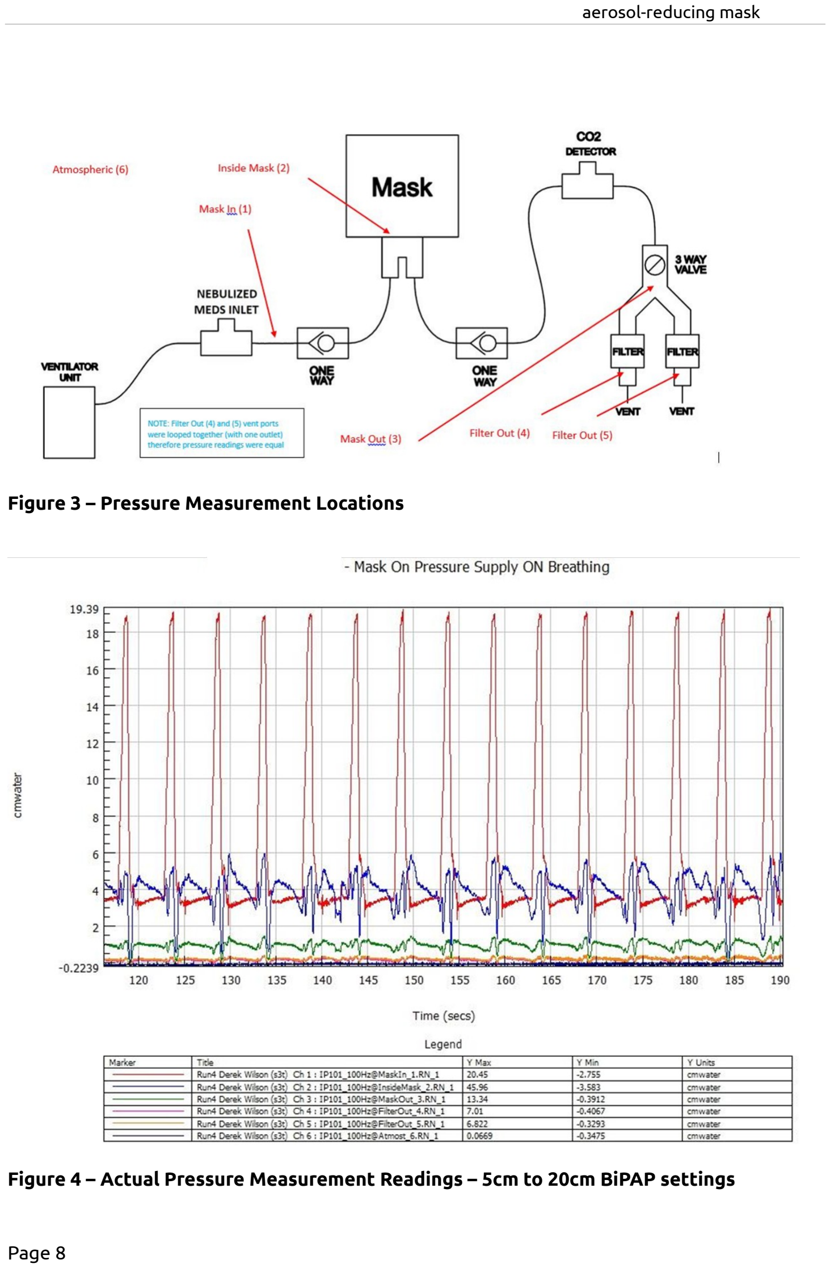
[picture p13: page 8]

Figure 3 – Pressure Measurement Locations

Figure 4 – Actual Pressure Measurement Readings – 5cm to 20cm BiPAP settings

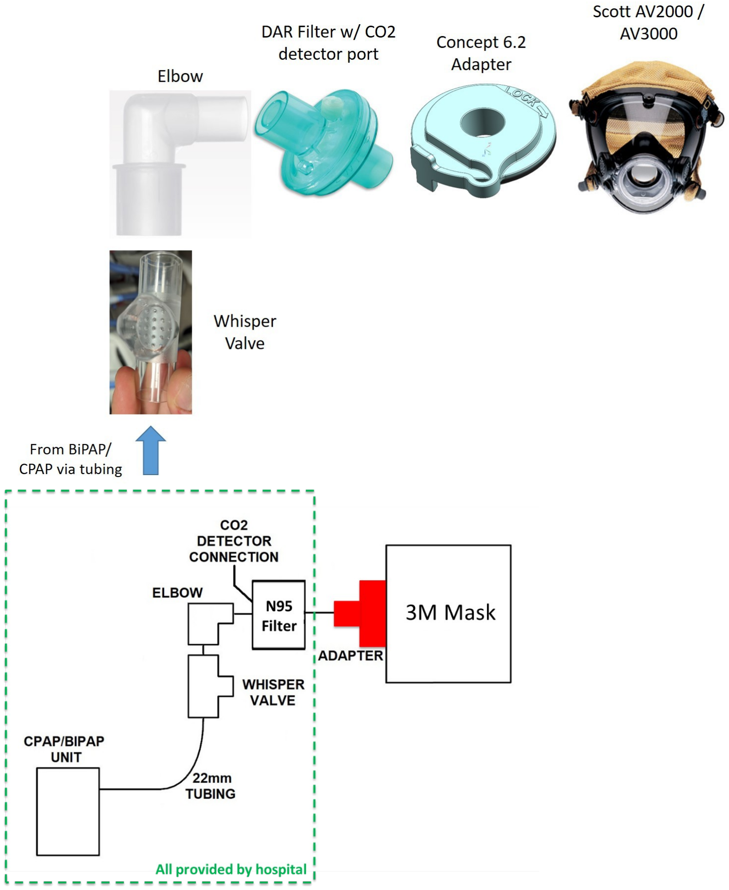
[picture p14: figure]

Figure 5 – Final Simplified Respiratory Circuit

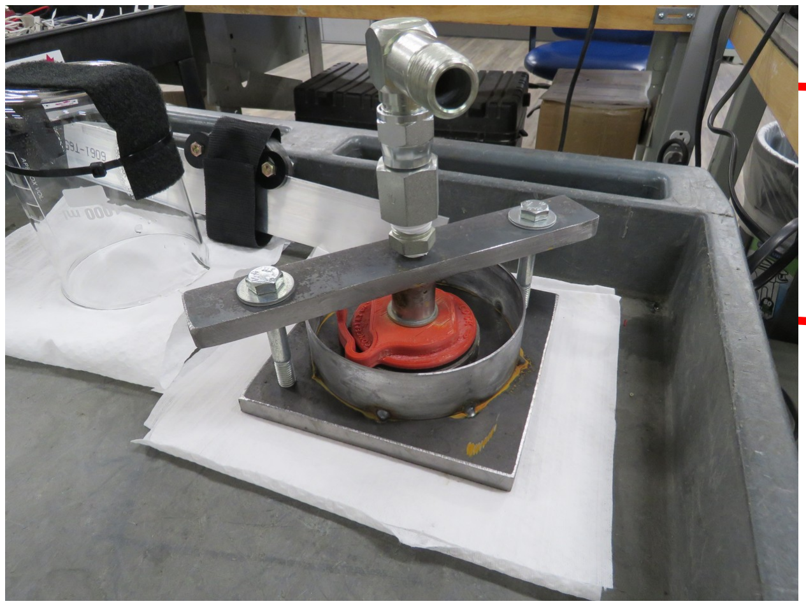
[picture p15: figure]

Figure 6 – 3DP Adapter Porosity testing

### Next steps

- Complete application and user guidance documentation.
- Once internal LHSC Ethics Application has been approved (estimated April 9th), the Medical Team will conduct their first testing on patients, in a controlled environment. Expecting to conduct 2 days of patient testing.
- Assuming controlled patient testing is successful, plan is to expand use across both London hospitals (University Hospital and Victoria Hospital). Predictive models identify April 15th as a date during which demand for invasive ventilation exceeds capabilities.
- Demonstrated success in both hospitals will then open opportunity to expand across Ontario and North America.

### Medical viability

The COVID-19 virus is spread primary with respiratory droplets, inhaled through one’s nasal or oral cavity into the respiratory tract. Aerosolization of respiratory droplets has also been identified as a major mechanism of transmission, and droplets containing virus can remain airborne for several hours. Procedures that aerosolize the COVID-19 virus significantly increase risk of transmission to health care workers. These procedures include placement and movement of a mask for NIPPV, suctioning upper airways and intubation of a patient for invasive ventilation. Given the concerns of aerosolization of viral particles, the American Society of Anesthesiology has recommended against use of NIPPV when a patient is suspected to have COVID19.

## Surround with water and look for bubbles around red

adapter.

## Pressurize to 30cmH20

Hospitals address these concerns in one of two ways. Firstly, patients may simply not be offered NIPPV, and instead are intubated and placed on a standard ventilator. This increases demands on an already scarce resource (invasive ventilators), while worsening patient outcomes when placing on a more aggressive therapy than necessary. The alternative option is to use the aerosolizing standard mask with NIPPV, and accept the risk this poses to health care workers and other patients.
The MAIN-COVID mask overcomes these challenges by providing a mask for NIPPV that reduces aerosolization. In doing so, a number of desirable outcomes emerge:
1. Decreases use of standard invasive ventilators, currently a scarce resource
2. Decreases health care worker associated infections
3. Decreases patient morbidity and mortality associated with use of a more aggressive therapy (invasive ventilation) than necessary (NIPPV)

### Patient Safety

The MAIN-COVID mask has been extensively tested. Testing has included:

1. At General Dynamics Land Systems (GDLS), the MAIN-COVID19 mask test was evaluated and passed a smoke test in a test dummy, as previous described
2. Pilot testing during which members of the research team were fit tested while wearing the mask, and supervised by respiratory therapists for mask leak at standard NIPPV pressures. Use of 5, 10, 15, 20 and 25 cm H2O pressure did not leak from the mask.
3. The MAIN-COVID19 mask was worn by standardized dummies in the GDLS lab, and no leak was found, using the spectrum of standard NIPPV settings.
4. A pilot patient study is undergoing at Western University April 12 onwards. Based on healthy human subject data (on investigators), 100 units have already been purchased, with a commitment for an additional 200 units. This was based on the reviews of the pulmonary medicine, emergency medicine and critical care physicians who observed the MAIN-COVID19 mask testing, and were universally in support of its’ broader use
5. Given the urgency of applying this essential technology broadly, a study will be ongoing during real-life application.

### Regulatory Processes

An application is being submitted to Health Canada for a Class II license. However, hospitals in Canada are not currently required to have Health Canada approval to use a new device, so long as efforts are in place to minimize aerosolization. Similarly, in the United States, the Food and Drug Administration (FDA) is allowing manufacturers of certain FDA-cleared ventilator devices to make modifications without making a new 510(k) submission. The following FDA recommendation excludes the MAIN-COVID19 mask from 510(k) submission (6):

“The use of devices indicated for sleep apnea (including the noncontinuous ventilators delivering continuous positive airway pressure (“CPAP”) or bi-level positive airway pressure), provided that appropriate design mitigations are in place to minimize aerosolization”
A Clinical trial has been registered with clincaltrials.gov.
The project is under review with Western's Health Sciences Research Ethics Board (HSREB) and with the Clinical Research Impact Committee (CRIC) at Lawson Health Science Institute.

### References

1. Doremalen N, Morris DH, Bushmaker T, Holbrook MG et al. Aerosol and Surface Stability
of SARS-CoV-2 as Compared with SARS-CoV-1. Correspondence with the Editor, New England Journal of Medicine. March 17 (2020): Available at: https://www.nejm.org/doi/full/10.1056/NEJMc2004973?url_ver=Z39.88-2003&rfr_id=ori:rid:crossref.org&rfr_dat=cr_pub%20%200pubmed (https://www.nejm.org/doi/full/10.1056/NEJMc2004973?url_ver=Z39.88-2003&rfr_id=ori:rid:crossref.org&rfr_dat=cr_pub%20%200pubmed)
2. World Health Organization. Coronavirus Disease 2019 (COVID-19) Situation Report- 66. March 26 (2020). Available at:https://www.who.int/docs/default-source/coronaviruse/situation-reports/20200326-sitrep-66-covid-19.pdf?sfvrsn=81b94e61_2 (https://www.who.int/docs/default-source/coronaviruse/situation-reports/20200326-sitrep-66-covid-19.pdf?sfvrsn=81b94e61_2)
3. Tran K, Cimon K, Severn M et al. Aerosol Generating Procedures and Risk of Transmission
of Acute Respiratory Infections to Healthcare Workers: A Systematic Review. Plos One 2012: 7(4): e35797. See Table 2, available at: https://www.ncbi.nlm.nih.gov/pmc/articles/PMC3338532/
4. American Society of Anesthesiologists. COVID-19 Resources for Anesthesiologists: Information for Health Care Professionals. Available at: https://www.asahq.org/about-asa/governance-and-committees/asa-committees/committee-on-occupational-health/coronavirus (https://www.asahq.org/about-asa/governance-and-committees/asa-committees/committee-on-occupational-health/coronavirus)
5. Hui DS, Chow BK, Lo T, Ng SS et al. Exhaled Air Dispersion During Noninvasive Ventilation via Helmets and a Total Facemask. Chest 2015: 147(5); 1336-1343. Available at: https://www.sciencedirect.com/science/article/pii/S0012369215383598
6. U.S. Department of Helath and Human Services, Food and Drug Administration, Center for Devices and Radiological Health. Enforcement Policy for Ventilators and Accessories and Other Respiratory Devices During the Coronavirus Disease 2019 (COVID-19) Public Health Emergency: Guidance for Industry and Food and Drug Administration Staff. March 2020. Available at: https://www.fda.gov/media/136318/download

### Appendix 1 – Initial Set of Requirements

Requirement | Compliance Statement
Solution shall allow connection of supplemental oxygen | Provided via the CPAP/BiPAP machine
Solution shall allow application of nebulized medications | Provide via appropriate adapter within 22mm respiratory circuit
Solution shall allow for ventilation through use of commonly available CPAP or BiPAP machines | Compliant
Solution shall allow for exit of 60 LPM outflow | Provided via the CPAP/BiPAP machine
Solution shall filter exhaust with N95 or better filter | Exceed requirement with medical DAR filters
Solution shall allow for testing of O2/CO2 levels | Provide via appropriate adapter within 22mm respiratory circuit
Solution shall prevent asphyxiation if CPAP/BiPAP is off | Provide via Whisper Valve within 22mm respiratory circuit
Solution shall cover eyes, nose, and mouth mucus membranes | Compliant with use of 3M Scot AV2000 Full Face Mask
Solution shall prevent escape of aerosolized particles while typically operating up to 25cmH2O pressure, and a maximum of 30cmH20 | Compliant per test data
Solution should fit 5th percentile female up to 95th percentile male | Designed for use with Small, Medium and Large AV2000 Face Masks
Solution shall be free of latex | Compliant
Solution shall be compatible with typical cleaning/disinfecting procedures (70% ethanol, 0.5% hydrogen peroxide, 0.1% sodium hypochlorite) | Compliant
Solution shall be made available as open source | Compliant on 3DP adapter
Solution should minimize damage to patients skin after prolong use | Better than half face masks due to substantially larger sealing surface
Solution shall be tailorable to different mask solutions based on availability | Tested solutions that use 3M Scot AV3000 & AV2000, Honeywell 7600, and NATO Gas Mask
Solution shall be easy to produce/procure | Uses common hospital components, a commercially available mask, and easily producible 3D printed adapter
Solution shall connect to standard respiratory therapy hoses, fittings, and adapters | System designed to be integrated into a respiratory system using 22mm tapered fittings (ISO+5367-2014 & ISO 5356-1 (4e 2015))

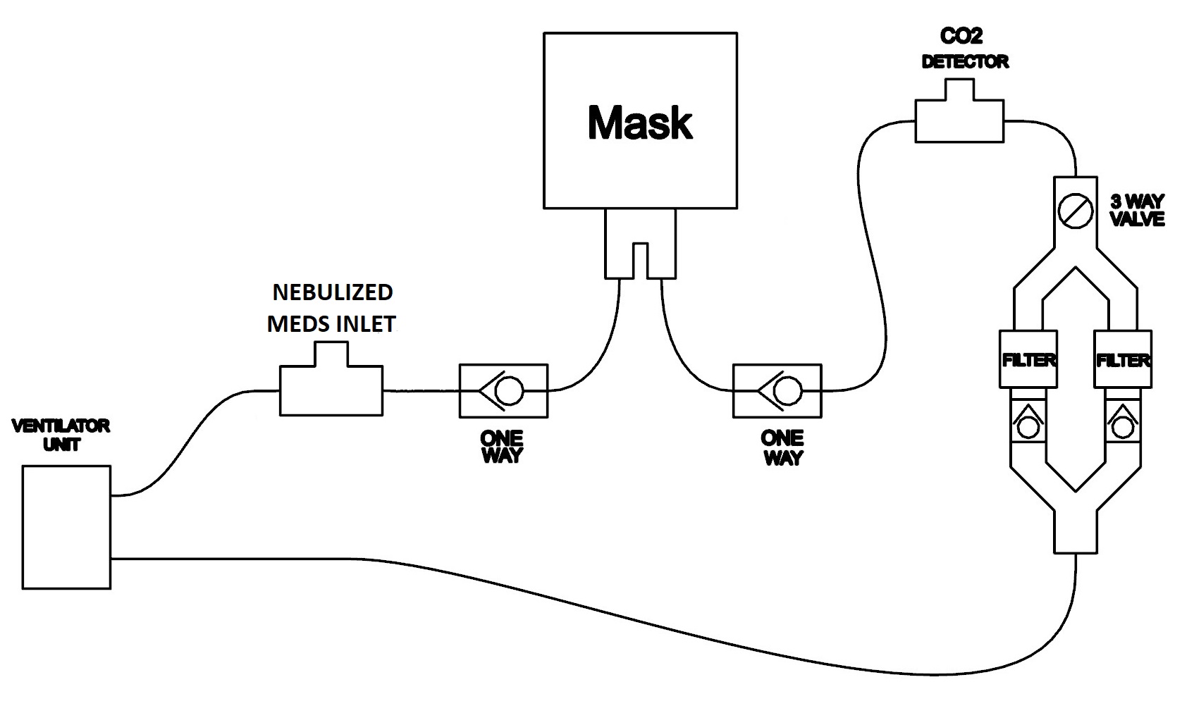
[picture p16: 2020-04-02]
planning/Diagram_Ventilator R1.jpg

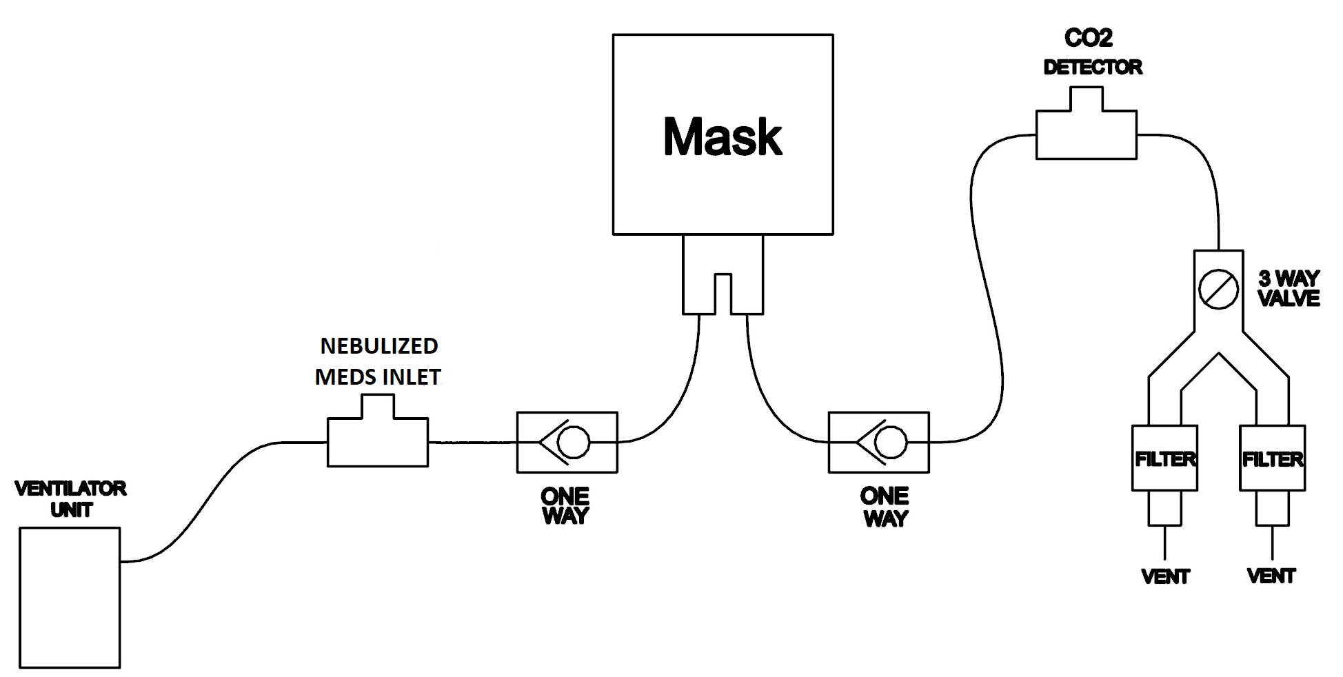
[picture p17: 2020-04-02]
planning/Diagram_CPAP and BiPAP R1.jpg

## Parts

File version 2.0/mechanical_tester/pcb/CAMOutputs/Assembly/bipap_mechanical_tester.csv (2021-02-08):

Qty | Value | Device | Package | Parts | Description | MF | MPN | OC_FARNELL | OC_NEWARK | POPULARITY
2 |  | MA03-2 | MA03-2 | LIMIT_1_2, LIMIT_3_4 | PIN HEADER |  |  | unknown | unknown | 15
3 |  | MA04-1 | MA04-1 | STEPPER_1, STEPPER_2, STEPPER_3 | PIN HEADER |  |  | unknown | unknown | 41
3 | 1182-A4988 | 1182-A4988 | A4988 | IC1, IC2, IC3 | A4988 Stepper Motor Driver Carrier
1 | ARDUINO-NANO-3.0 | ARDUINO-NANO-3.0 | ARDUINO-NANO-3.0 | M1 | Arduino Nano 3.0
1 | SPRING_TB_RT2 | SPRING_TB_RT2 | SPRING_TB_RT2 | U$1 | Spring Loaded Terminal Block

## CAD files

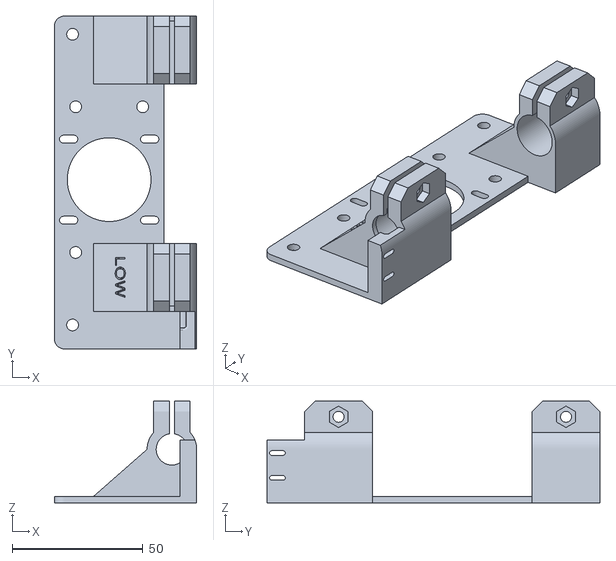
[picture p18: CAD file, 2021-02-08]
version 2.0/mechanical_tester/low_mount_main.stl
54.5 x 127.4 x 39.0

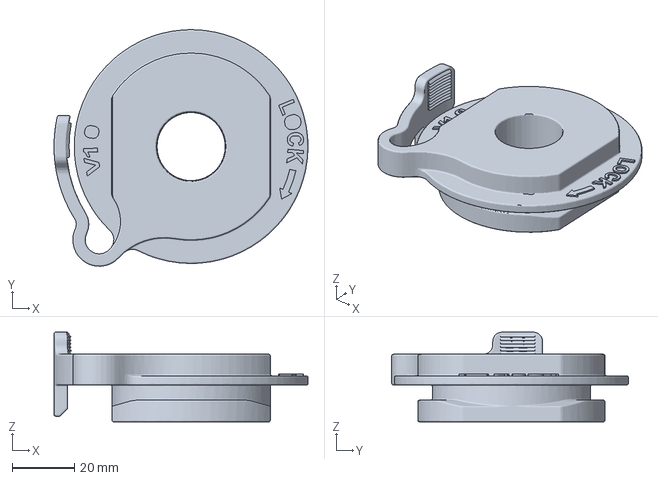
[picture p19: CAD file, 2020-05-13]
adapter.3mf
81.5 x 75.9 x 28.8 mm

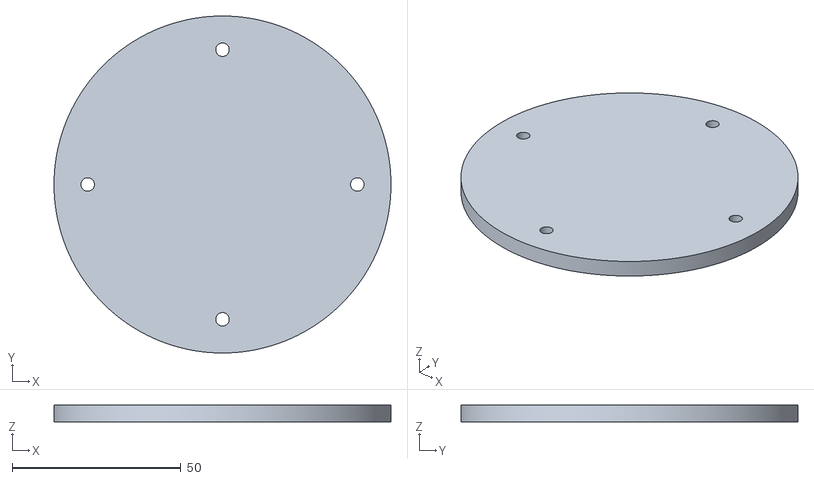
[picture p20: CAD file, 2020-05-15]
quality_assurance/submersion_test/stl/submersion_test_rig_bottom.stl
100.0 x 100.0 x 5.00

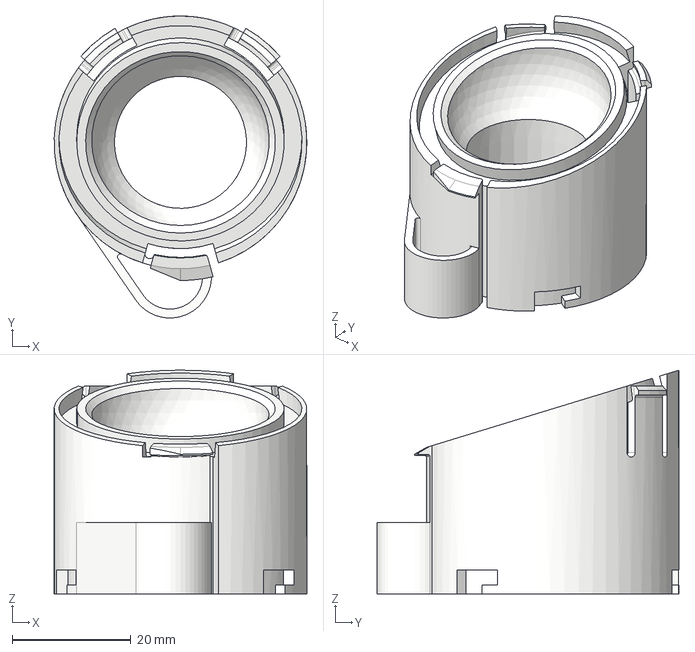
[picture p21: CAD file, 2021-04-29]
version 2.0/bipap_expiratory_port v47.step
42.6 x 50.9 x 37.7 mm

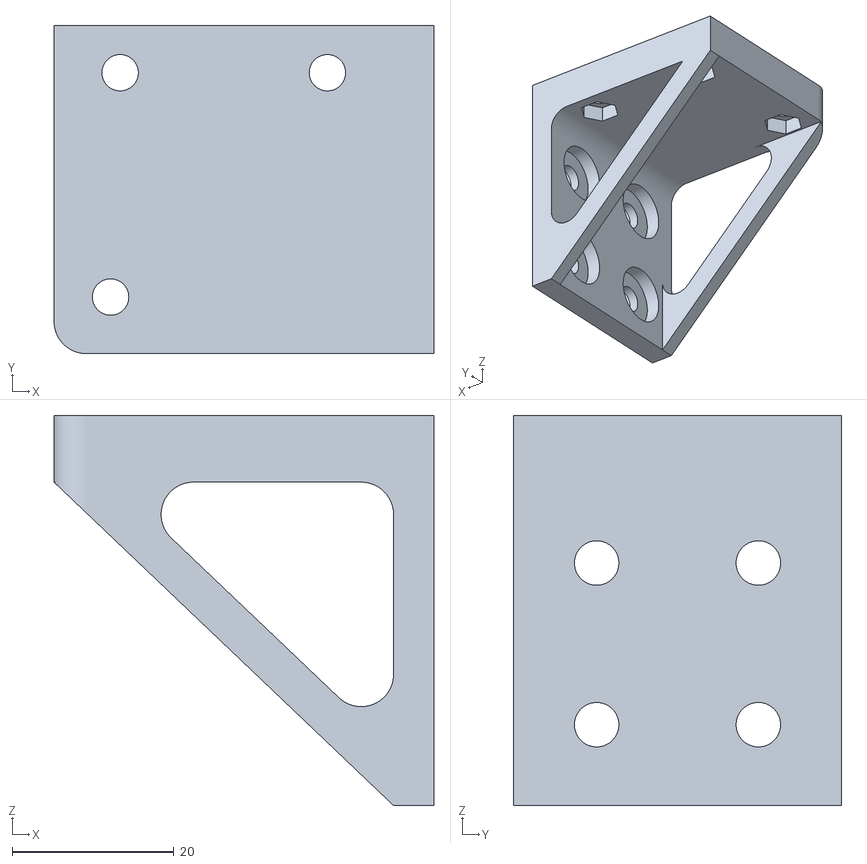
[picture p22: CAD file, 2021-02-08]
version 2.0/mechanical_tester/low_mount_bracket_mirror.stl
47.0 x 40.6 x 48.2

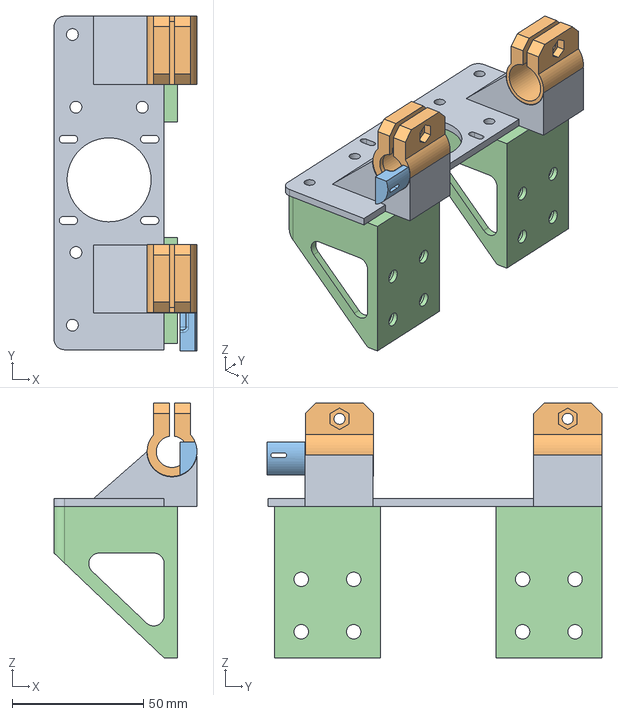
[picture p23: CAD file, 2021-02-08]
version 2.0/mechanical_tester/step_files/high_mount.step
54.5 x 127.6 x 97.2 mm

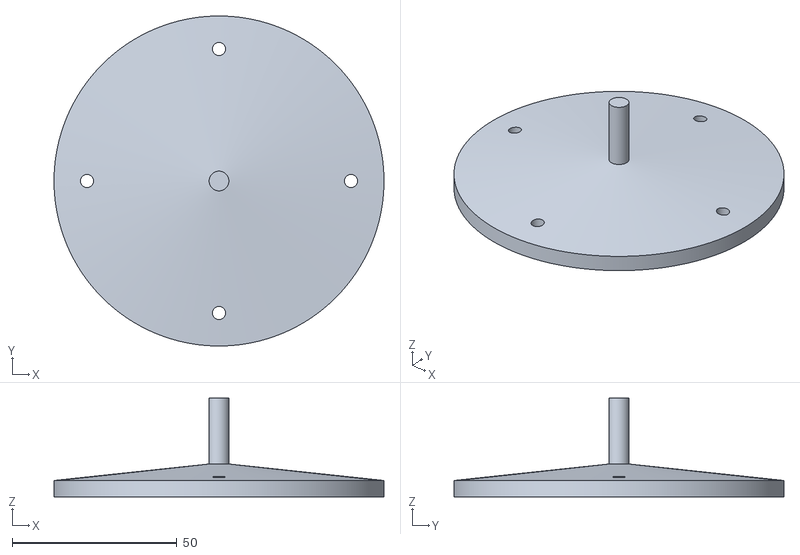
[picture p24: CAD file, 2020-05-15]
quality_assurance/submersion_test/stl/submersion_test_rig_top.stl
100.0 x 100.0 x 30.0

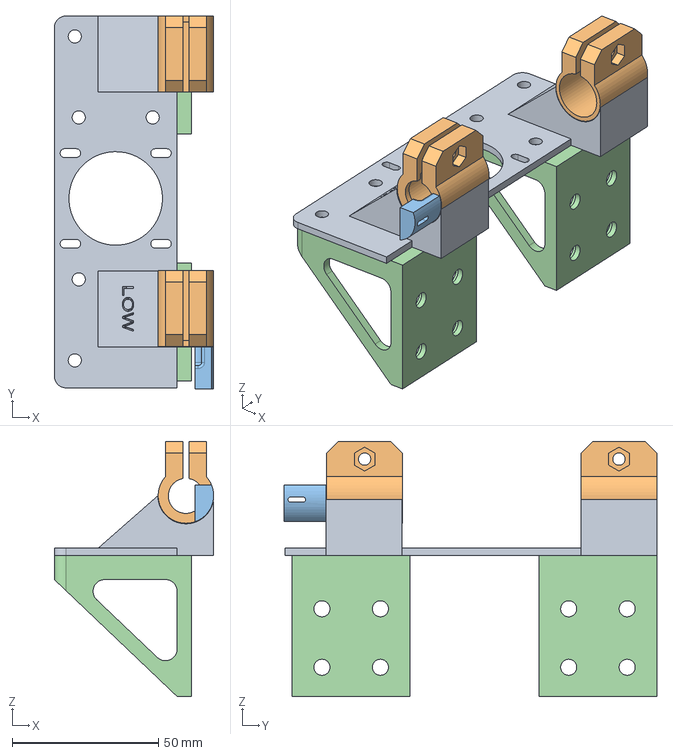
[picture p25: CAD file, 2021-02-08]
version 2.0/mechanical_tester/step_files/low_mount.step
54.5 x 127.6 x 87.2 mm

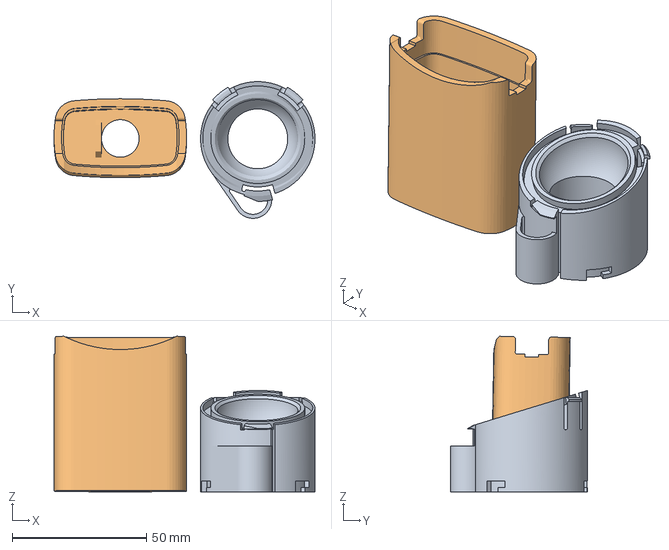
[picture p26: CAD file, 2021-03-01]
version 2.0/bipap_inspiratory_expiratory_ports.3mf
97.3 x 50.9 x 58.0 mm
bipap_expiratory_port.stl
bipap_inspiratory_port.stl

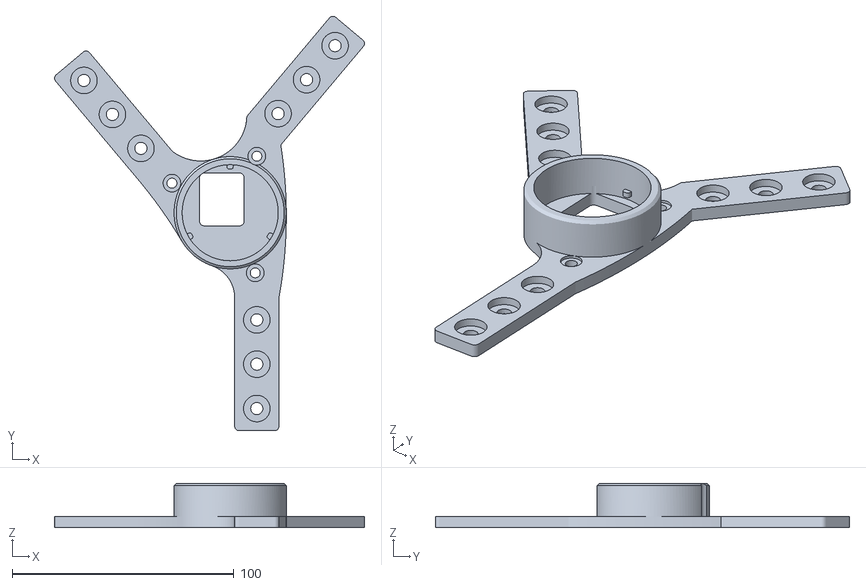
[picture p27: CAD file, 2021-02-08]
version 2.0/mechanical_tester/port_collet_1.stl
139.8 x 186.9 x 20.0

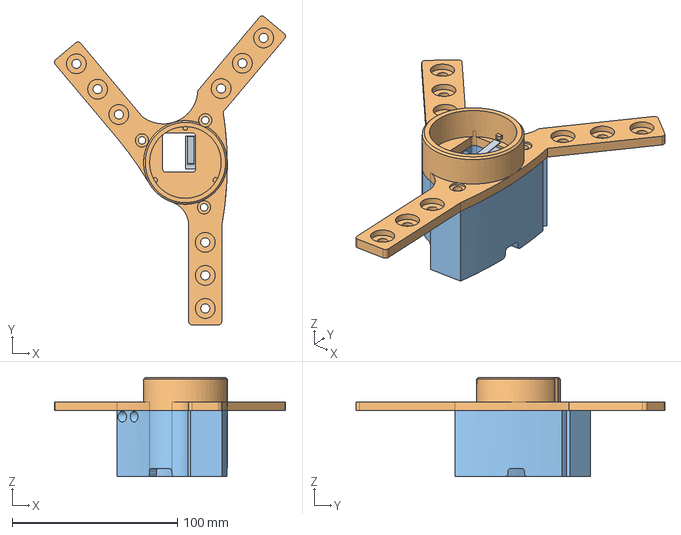
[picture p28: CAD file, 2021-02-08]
version 2.0/mechanical_tester/step_files/port_collet.step
139.8 x 186.9 x 60.0 mm

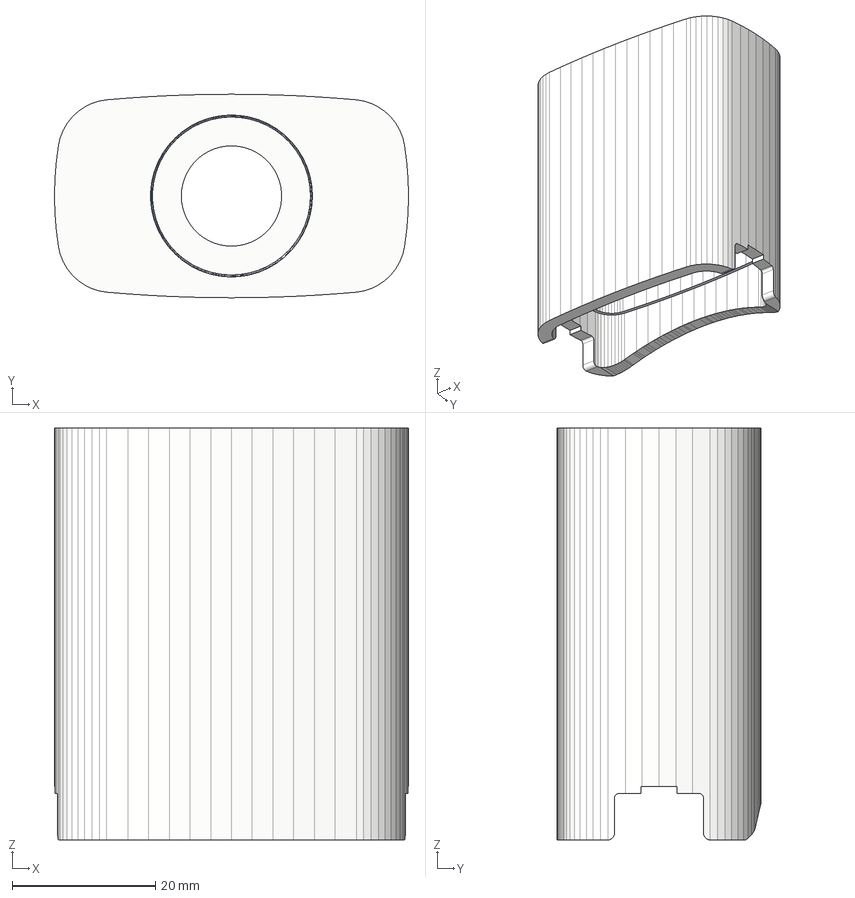
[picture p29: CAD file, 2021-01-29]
version 2.0/bipap_inspiratory_port.step
49.4 x 28.4 x 57.5 mm

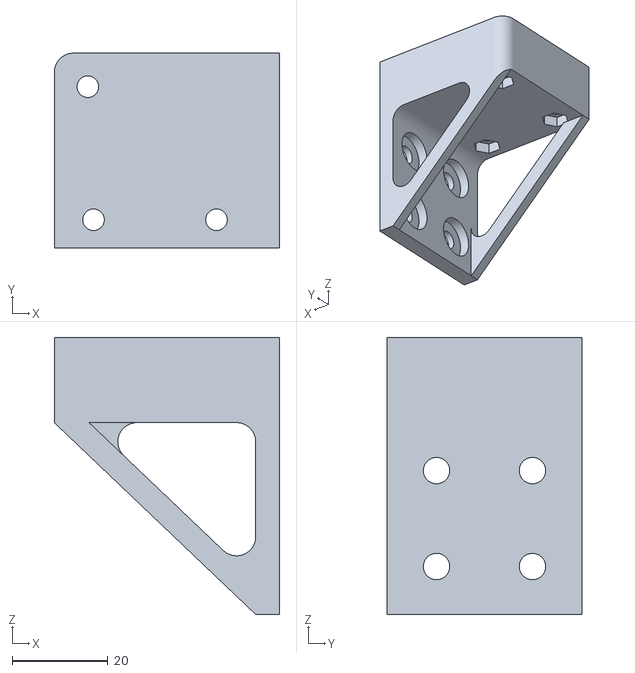
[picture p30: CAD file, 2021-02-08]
version 2.0/mechanical_tester/high_mount_bracket.stl
47.0 x 40.6 x 57.8

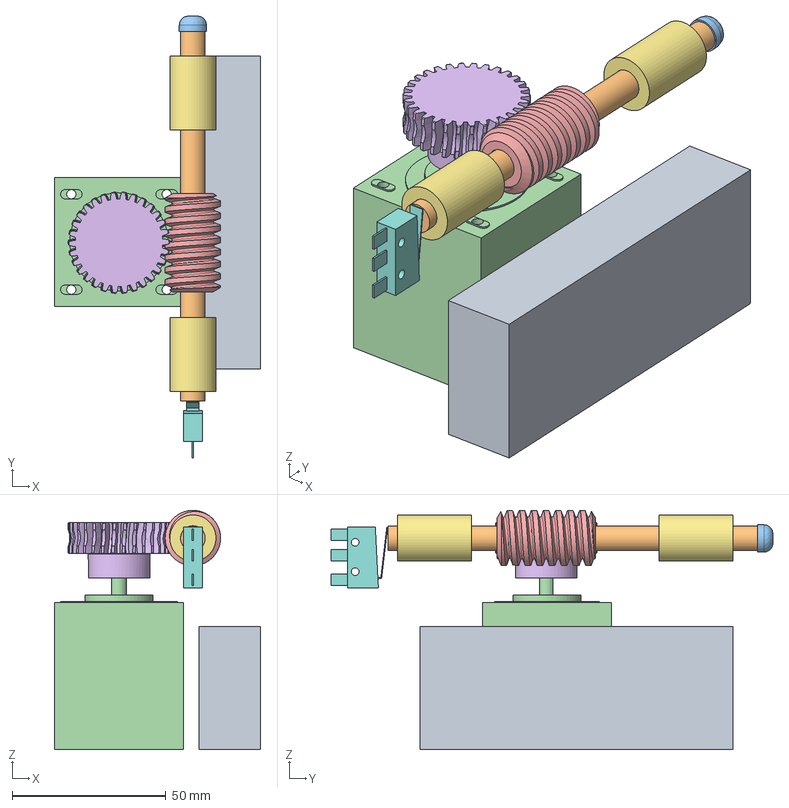
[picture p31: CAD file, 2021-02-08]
version 2.0/mechanical_tester/step_files/low_actuator.step
67.0 x 143.6 x 77.7 mm
piston
simple_nema_17 v1
57545K646_METAL WORM GEAR
4037N131_PLASTIC WORM GEAR
linear_bearings

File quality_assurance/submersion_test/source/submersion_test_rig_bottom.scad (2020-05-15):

// Include variables
include <submersion_test_rig_variables.scad>;
include <submersion_test_rig_common.scad>;

// Create bottom plate
module bottom_plate() {
    cylinder(5, plunger_diameter / 2, plunger_diameter / 2, $fn=360);
}

difference() {
    bottom_plate();
    holes(); // Found in common
}

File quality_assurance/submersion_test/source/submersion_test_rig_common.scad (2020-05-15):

// Create holes in 4 quadrants
module holes() {
    translate([hole_distance_from_centre , 0, 0]) cylinder(10, hole_diameter / 2, hole_diameter /2, $fn=360);
    translate([-hole_distance_from_centre , 0, 0]) cylinder(10, hole_diameter / 2, hole_diameter /2, $fn=360);
    translate([0, hole_distance_from_centre , 0]) cylinder(10, hole_diameter / 2, hole_diameter /2, $fn=360);
    translate([0, -hole_distance_from_centre , 0]) cylinder(10, hole_diameter / 2, hole_diameter /2, $fn=360);
}

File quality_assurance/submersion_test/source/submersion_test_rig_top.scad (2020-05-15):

// Include variables
include <submersion_test_rig_variables.scad>;
include <submersion_test_rig_common.scad>;

// Create top plunger
module plunger() {
    union() {
        cylinder(30, collet_diameter / 2, collet_diameter / 2, $fn=360);
        cylinder(5, plunger_diameter / 2, plunger_diameter / 2, $fn=360);
        translate([0, 0, 5]) cylinder(5, plunger_diameter / 2, collet_diameter / 2, $fn=360);
    }
}

difference() {
    plunger();
    holes(); //Found in common
}

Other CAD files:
version 2.0/mechanical_tester/high_mount_main.stl
version 2.0/bipap_expiratory_port.stl
version 2.0/mechanical_tester/port_collet_2.stl
version 2.0/mechanical_tester/piston_cap.stl
quality_assurance/submersion_test/source/submersion_test_rig_variables.scad
source/adapter.stl
version 2.0/bipap_expiratory_port v47.f3d
version 2.0/bipap_inspiratory_port.stl
version 2.0/mechanical_tester/4037N131_pinion.stl
version 2.0/mechanical_tester/4in_cut_guide.stl
version 2.0/mechanical_tester/circuit_housing_body.stl
version 2.0/mechanical_tester/circuit_housing_cover.stl
version 2.0/mechanical_tester/e-stop_housing.stl
version 2.0/mechanical_tester/high_mount_bracket_mirror.stl
version 2.0/mechanical_tester/low_mount_bracket.stl
version 2.0/mechanical_tester/mount_support_low.stl
version 2.0/mechanical_tester/step_files/4037N131_PLASTIC WORM GEAR.step
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

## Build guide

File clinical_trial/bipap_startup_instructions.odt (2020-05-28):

Bipap startup instructions

Plug in device when possible

Turn on device with button in back

Enable clinical mode by pressing and holding centre button and setup button simultaneously. Set to 5 minutes.

Disable “non-vented mask” alarm by clicking “setup” several times until you reach the “AlarmSettings” page

Ensure all other alarms are on

Press setup until you arrive to “clinical settings”, then Advanced Settings

Select “mask type”, and then “full face mask”

Attach circuit

Learn circuit

Push 'lung' button

Hit Start button

Attach tube to patient mask

Consent

Fill patient info sheet with patient (demographics)

Prepare circuit

Attach mask

Rapid removal training

Start

Updated: 2020 April 18

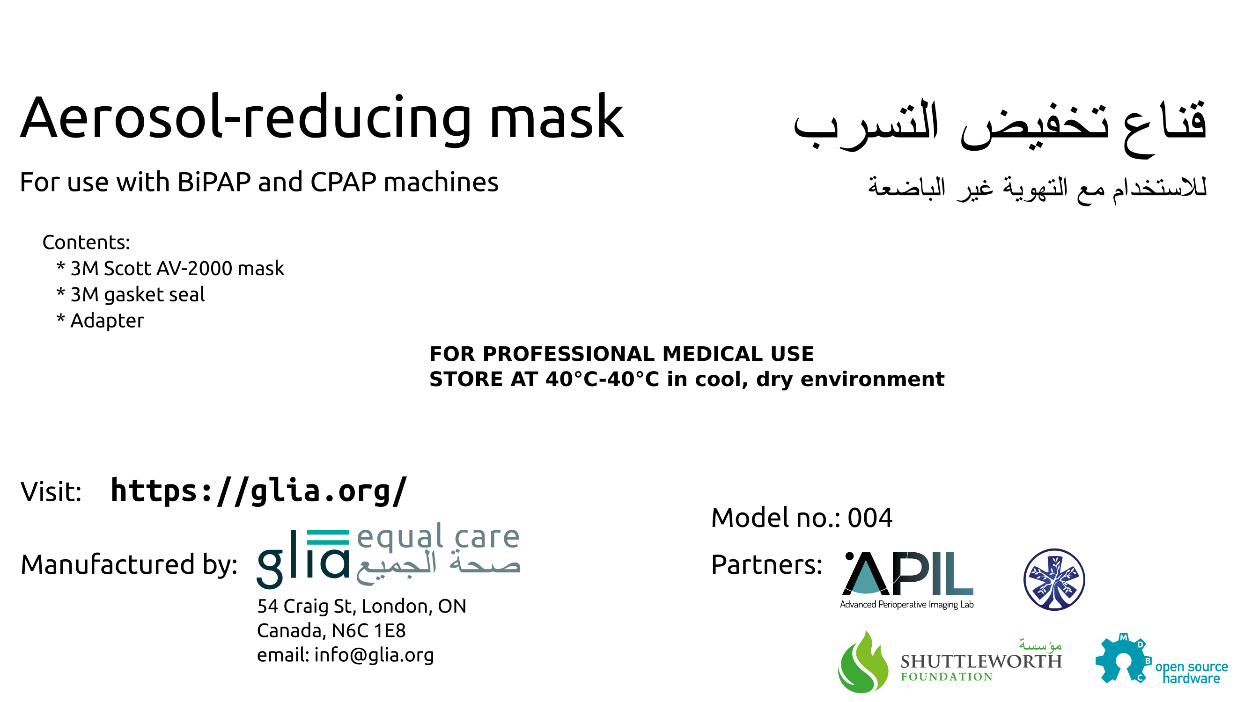
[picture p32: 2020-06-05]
manual/device_label.png

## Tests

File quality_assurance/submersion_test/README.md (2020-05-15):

* Print test rig
* Attach to CNC or other machine
* Get GCode from here: https://github.com/mef51/bleachbath

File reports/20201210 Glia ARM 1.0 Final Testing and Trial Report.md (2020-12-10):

---
tags: Glia-ARM, Testing, ISO, FDA, UHN
---
# 20201210 Final Report of Device Testing and Clinical Trial Data from Glia Aerosol-Reducing Mask (ARM) v1.0 for Non-invasive Ventilation



1. ISO 17510:2015 Annexes B-F
2. Achievable FiO2
3. Clinical trial

Report date: 2020.12.10

Azad Mashari, Maggie Xiao, Vahid Anwari, Ben Thomson 

## 1. ISO 17510:2015 Report
Testing performed 29 September - 30 October 2020, by Vahid Anwari and Azad Mashari at Toronto General Hospital and Thornhill Laboratories, under supervison of Azad Mashari MD FRCPC, Staff Anesthesiologist, Toronto General Hospital, University Network. 

### General Set-up
#### Head Phantom
A head phantom was custom built by silicon casting from 3D printed molds (figure 1.1). The phantom was equipped with two sensor ports: 
1. A reversed standard 22 mm airway taper at the mouth allowing an in-line pressure/flow sensor to be inserted from the back.
2. A pressure or gas sampling port at the nose, consisting of the barrel of a 3 ml syringe connected to pressure tubing with a luer connector.

1.1 Head Phantom - front
***Fig 1.1**. Test phantom - front view showing pressure-flow (mouth) and pressure/gas sampling (nose) ports*.

1.2. Head Phantom - back
***Fig 1.2**. Test phantom - rear view Airway tubing is connected to FluxMed sensor. Sample tubes for the FluxMed and the pressure/gas sensor pass through the bottom of the neck*.

#### Viral filters
System was tested with two different viral filters compatible with the the ARM. These models were selected due to their availability and their low flow resistance values. Flo-Guard has the lowest resistance in an N95 filter. Hydro-Guard Mini has a resistance value typical of most models on the market.
* Intersurgical Hydro-Guard Mini 
    * [Manufacturer Page](https://fda.report/MAUDE/MDR/7742777)
        * Filtration Efficiency: >99.999%
        * Resistance at 30L/min: 1.3 cm H2O
        * Resistance at 60L/min: 2.9 cm H2O
        * Compressible volume: 63 ml
        * Minimum tidal volume: >200ml
        * Weight: 30 g
        * Connectors: 22F/15M-22M/15F
    * [FDA Report](https://fda.report/MAUDE/MDR/7742777)
* Intersurgical Flo-Guard. 
    * [Manufacturer Page](https://https://www.intersurgical.com/products/airway-management/floguard-low-resistance-breathing-filter-for-cpap-and-bilevel)
        * Filtration efficiency: >99.99%
        * Resistance at 30L/min: 0.4 cm H2O
        * Resistance at 60L/min: 0.8 cm H2O
        * Resistance at 120L/min: 2.0 cm H2O
        * Resistance at 240L/min: 5.1 cm H2O
        * Compressible volume: 80ml
        * Weight: 27.8g
    * [FDA Report](https://fda.report/PMN/K121026)

#### Anti-asphyxia valve (required in some configurations)
* Resmed Leak valve 24991: [FDA](https://fda.report/GUDID/00619498249916) 

#### Flow and pressure sensor: 
* FluxMed GrH: [Manufacturer Page](https://https://mbmed.com/fluxmed-grh/)

### Annex B: Exhaust Flow 
September 29, 2020, Toronto General Hospital, Hyperbaric Medicine Unit. 
#### Objective
Define relationship between pressure provided to patient and exhaust flow 
#### Apparatus & Set-up
* ARM Mask: AV2000 M, 3M Lot #031120 FT 936
* ARM Gasket and Adapter V1.0. ABS. Black.
* Filters
    * Intersurgical Hydro-Guard Mini 
    * Intersurgical Flo-Guard 
* Anti-asphyxia valve: Resmed Leak valve
* Flow and Pressure Sensor: FluxMed GrH (s/n 2802020022)

B1. Annex B testing set-up 
***Fig B1**. Exhaust flow testing set-up with Hydro-mini filter. FluxMed sensor is connected at patient connection port. Wall oxygen (via a sequence of adapters) is connected to FluxMed. Flow readings are recoded from FluxMed sensor. Connection sequence: Seal - Mask - Gasket - Adaptor - Filter (Flo-Guard | Hydro-Guard Mini) - Asphyxiation valve ( No | Yes ) - FluxMed sensor - Flow source*

#### Procedure
1. Sensor was positioned at the Patient Connection Port 
2. To exclude flow source, the patient interface was sealed with plastic wrap (between the head mannequin and the mask)
3. Flow rate was adjusted to achieve the minimum pressure (5 cm H2O) in the RATED pressure range (0-40 cm H2O), pressure was measured at this point. 
4. Step 3 was repeated at the following pressures: 10, 15, 20, 25, 30, 35, 40 cm H2O.
5. Flow rates were averaged over 10 seconds at sampling frequency of 8 Hz
#### Results
##### Series 1: Dual-limb ventilator configuration – Flo-Guard
Filter: Intersurgical Flo-Guard (Lot #32053172). 
Asphyxiation Valve: None 
|Trial|Target Pressure<br>(cm H2O)|Actual Pressure<br>(cm H20)|Required Flow<br>(L/min)|
|-|-|-|-|
|1.1|5|5.0|0.0|
|1.2|10|10.1|0.1|
|1.3|15|15.1|0.0|
|1.4|20|20.0|0.1|
|1.5|25|25.0|0.2|
|1.6|30|30.0|0.0|
|1.7|35|35.0|0.0|
|1.8|40|40.0|0.2|

##### Series 2: Single-limb ventilator configuration - Flo-Guard
Filter: Flo-Guard (Lot #32053172). 
Asphyxiation valve: Resmed

|Trial|Target Pressure<br>(cm H2O)|Actual Pressure<br>(cm H2O)|Required Flow<br>(L/min)|
|-|-|-|-|
|2.1|5|5.3|25.0|
|2.2|10|10.0|34.5|
|2.3|15|14.9|41.4|
|2.4|20|20.0|47.3|
|2.5|25|24.8|52.3|
|2.6|30|30.0|56.7|
|2.7|35|35.6|62.3|
|2.8|40|40.3|67.4|

##### Series 3: Dual-limb ventilator configuration – Hydro-Guard Mini
Filter: Hydro-Guard Mini Lot# 32053312
Asphyxiation valve: None

|Trial|Target Pressure<br>(cm H2O)|Actual Pressure<br>(cm H2O)|Required Flow<br>(L/min)|
|-|-|-|-|
|3.1|5|5.5|1.1|
|3.2|10|10.0|1.0|
|3.3|15|15.0|0.8|
|3.4|20|20.0|1.0|
|3.5|25|25.0|1.1|
|3.6|30|30.0|0.9|
|3.7|35|35.0|1.1|
|3.8|40|40.0|0.9|

##### Series 4: Single-limb ventilator configuration – Hydro-Guard Mini
Filter: Hydro-Guard Mini; Lot# 32053312
Asphyxiation valve: Resmed (Lot #)
Date: Tues 29 Sept,2020, 12:30 pm

|Trial|Target Pressure<br>(cm H2O)|Actual Pressure<br>(cm H2O)|Required Flow<br>(L/min)|
|-|-|-|-|
|4.1|5|5.3|23.6|
|4.2|10|9.8|32.3|
|4.3|15|15.2|40.3|
|4.4|20|20.0|46.2|
|4.5|25|25.3|51.5|
|4.6|30|30.0|55.5|
|4.7|35|35.0|59.7|
|4.8|40|40.2|65.0|

### Annex C: Resistance to flow
October 2, 2020, 10:30 AM

#### Objective
Measure pressure drop between source and patient airway
#### Apparatus & Set-up
* Flo-Guard Lot# 32053312
* Hydro-Guard Mini Lot# 32053312
* Sensor 1: FluxMed GrH (s/n 2802020022) – Patient-Connection Port 
* Sensor 2: FluxMed GrH (s/n 2802019032) – Airway 

C1. Annex C testing set-up
***Fig C1**. Flow resistance set-up*. 

#### Procedure
1. Set-up as shown in Figure C1. Patient interface was open to the atmosphere to achieve the specified flowrates.
1. Flow/Pressure sensors were placed at the patient connection port (visible in image) and inside the mannequin in the mouth (line coming from the bottom of the mannequin visible) 
1. At the target flow rate of 50 l/min, pressure measurements were averaged at a 10 second interval (8 Hz sampling rate) and the pressure delta recorded.
1. The test was repeated with saturated filters.  Filters were soaked in a water bath for 10 minutes. removed, excess water drained and tested as above. 

#### Results
|Filter|State|Patient Connection Port Flow<br>(L/min)|Patient Connection Port Pressure<br>(cm H2O)|Airway Flow<br>(L/min)|Airway Pressure<br>(cm H2O)|**Pressure difference**<br>**(cmH2O)**|
|-|-|-|-|-|-|-|
|Flo-Guard|Dry|50.1|0.7|41.2|0.8|**0.1**|
|Flo-Guard|Dry|100.1|1.5|79.0|1.5|**0.0**|
|Flo-Guard|Wet|50.0|0.9|40.4|0.7|**0.2**|
|Flo-Guard|Wet|100.3|1.8|40.1|2.1|**0.3**|
|Hydro-GuardMini|Dry|50.4|2.1|41.5|0.72|**1.4**|
|Hydro-GuardMini|Dry|100.3|4.5|79.5|1.45|**3.1**|
|Hydro-GuardMini|Wet|50.1|2.3|41.7|0.7|**1.6**|
|Hydro-GuardMini|Wet|100.3|5.1|80.1|1.6|**3.5**|

### Annex D: Anti-Asphyxia Valve Opening and Closing Pressures
Tuesday 29 Sept 2020. Toronto General Hospital

#### Objective
Determine the pressures at which the anti-asphyxia valve opens and closes to atmosphere 
#### Apparatus & Set-up
D1. Annex D test set-up
***Fig D1**. Anti-asphyxia valve opening and closing pressure measurement set-up*.
#### Procedure
##### Opening Pressure
Set up is shown in figure D1, the FluxMed sensor was attached between anti-asphyxia valve and flow source. 

Pressure was increased until the anti-asphyxia valve closed to atmosphere, the closing pressure was recorded.  Pressure was then decreased until the valve opened, the opening pressure was recorded.  The test was repeated for both the Flo-Guard and Hydro-Guard filters.

##### Closing Pressure
Starting with no flow and the anti-asphyxia valve open, flow was gradually increased until valve closure. Pressure at closure was documented for each filter. 

#### Results
|Filter|Opening Pressure<br>(cm H2O)|Opening Flow<br>(L/min)|Closing Pressure<br>(cm H2O)|Closing Flow<br>(L/min)|
|-|-|-|-|-|
|Flo-Guard|2.2|13.4|36.8|103.0|
|Hydro-Guard Mini|4.8|21.1|44.7|98.9|

### Annex E Determination of the inspiratory and expiratory resistance under single fault condition 
Friday 2 October 2020, 12:00 pm Toronto General Hospital 

#### Objective
To determine the inspiratory and expiratory resistance at a flowrate of 50 l/min in single fault condition.

#### Apparatus & Set-up
* Flo-Guard
* Hydro-Guard Mini
* Anti-aphyxia valve: Resmed
* Fluxmed sensor in mannequin airway (mouth)
* Wall suction (Inspiratory flow source)
* Wall oxygen (Expiratory flow source)

E1a. Annex E Expiratory Resistance Set-up
***Fig E1a**. Expiratory resistance set-up*. 

E1b. Annex E Expiratory Resistance Set-up Schematic
***Fig E1b**. Expiratory resistance set-up schematic*. 

E2a. Annex E Inspiratory Resistance Set-up
***Fig E2a**. Inspiratory resistance set-up*. 

E2b. Annex E Inspiratory Resistance Set-up Schematic
***Fig E2b** Inspiratory resistance set-up schematic*

#### Procedure
A filter and anti-asphyxia valve were connected to the ARM device. The free end of the anti-asphyxia valve was sealed with plastic film to simulate obstruction of the ventilator flow source.
1. Expiratory resistance (Fig E1a, E1b): an oxygen line was connected to the phantom airway and adjusted to obtain an out-flow of approximately 50 L/min, measured by the FluxMed sensor in the phantom airway. The achieved pressure and flow were recorded.
1. Inspiratory resistance (Fig E2a, E2b): a suction line was connected to the phantom airway and adjusted to obtain a flow of approximately 50L/min, measured by the FluxMed sensor in the phantom airway. The achieved pressure and flow were recorded.
   
#### Results
|Filter|Inspiratory Flow<br>(L/min)|Inspiratory Pressure<br>(cm H2O)|Expiratory Flow<br>(L/min)|Expiratory Pressure (cm H2O)|
|-|-|-|-|-|
|Flo-Guard|-49.8|-1.3|50.2|0.6|
|Hydro-Guard Mini|-49.3|-4.4|50.1|1.8|

### Annex F: CO<sub>2</sub> Rebreathing 
October 30, 2020 9:00-16:30

Azad Mashari, Vahid Anwari, Ben Thomson, Drew Miller (Thornhill)

Thornhill Medical Labs, Mars Building, 661 University Ave. 2nd Floor Toronto, Ontario 

#### Objective
To document safety of the device against CO2 rebreathing under normal function and relevant single fault conditions. 
Three supported configurations were tested: 
1. Mask and filter only
2. BVM configuration with PEEP valve
3. Single-limb NIV configuration (with anti-asphyxiation valve)

#### Set-up
F1. Annex F CO2 Rebreathing Set-up Schematic
***Fig F1**. Set-up for Annex F testing, CO<sub>2</sub> rebreathing. No mixing chamber ("~10L MIX Ch.") was included. Components described further in text.*

1. Breathing simulator: ASL5000 
    * Mode: Volume Pump
    * VT 500ml
    * RR 15
    * I:E 1:2 
    * FRC (URC) 1.5 L.
2. Gas analyzer: Oxisoft  EIN0016 SN:O2-03504; Software 0.8.4 
    * Calibrated for CO2 and O2
    * Sampling flow 280 mL/min. Set to match CO2 flow titrated at baseline 
    * Data collected at 10Hz. 
3. Pressure & flow sensor: Fluxmed GrH SN:2802020022
    * Caliberated
    * Recording at 16Hz
4. CPAP ventilator: Respironics REMstar auto Intl. REF 551P SN: P04341300C18D. 
    * Mode: CPAP 
    * Ramp: Off 
    * Flex type: None 
    * Tubing Type 22mm 1.9m (fixed) 
5. CO2 supply: 4.02% O2 with balance (95.98%) CO2. Connected by 50 foot, 1/4 inch ID tube to flux med. Flow meter inserted in-line (SFM 4300)
 
#### Results
values averaged over 15 simulated breaths (1 minute). Sampled at 10Hz. 

#### 0. Baseline (No device on manniqu)
End-tidal CO<sub>2</sub> after titration [mean(SD)]: 5.04(0.01)%
CO2 flow (1 minute average at 30Hz): 279(2) ml/min

#### 1. Mask & filter only
|Trial|Condition|ETCO2 max [mean(SD)]%|% Increase|
|---|---|---|---|
|0.0|Baseline: No Mask|5.04(0.01)|0
|0.1|Mask only|5.86 (0.02)|16.3|
|1.1|Flo-guard dry|7.81 (0.02)|55.0|
|1.2|Flo-guard wet|7.89 (0.02)|56.5|

#### 2. BVM (Ambu with PEEP valve)
No single fault test applicable since no flow is generated and there is no breathing tube to be blocked.

|Trial|PEEP Set|PEEP Actual|ETCO2 max [mean(SD)]%|% Increase|
|---|---|---|---|---|
|2.1|0|0|8.26 (0.2)|**63.9**|
|2.2|20|20.8|8.11 (0.02)|**60.9**|

Acceptable increase is < 20%. **BVM configuration does not meet requirements**.

#### 3. CPAP with anti-asphyxia valve and oxygen connector (capped off)

|Trial|CPAP Pressure (cm H2O)|ETCO2 max [mean(SD)]%|% Increase|
|---|---|---|---|
|3.1|5|5.70 (0.2)|13.1|
|3.2|10|4.31 (0.2)|**-14.5**|
|3.3|20|2.3 (0.2)|**-54.4**|

Note with CPAP support > 5 cm H<sub>2</sub>O, ETCO<sub>2</sub> reading dropped below baseline.

##### Single Fault CPAP tests
|Trial|Fault|ETCO2 max [mean(SD)]%|% Increase|
|---|---|---|---|
|3.4|Patient connection port occluded|8.35 (0.03)|**65.7**|
|3.5|CPAP connected with no flow|8.35 (0.01)|**65.7**|

Acceptable increase in single fault mode is <60%. **Mask does not meet single fault requirements** for unmonitored use.

## 2. Achievable FiO2 Testing
### Objective
To evaluate achievable FiO<sub>2</sub> with home CPAP configurations with supplimental oxygen.

### Set-up
* Set-up identical to CO<sub>2</sub> rebreathing trials (figure F1). 
* Configurations and settings for Breathing simulator unchanged (Vt: 500ml; RR: 15; I:E 1:2). 
* O<sub>2</sub> sensor in pharynx (30 ml deadspace to mouth).
* Trough values extracted for each breath. Average of 15 breaths (1 minute) after equilibraration (typically 3 minutes)

### Results

| Oxygen Flow (L/min) | CPAP (cm H<sub>2</sub>O) | Minimum FiO<sub>2</sub>% |
|---------------------|---------------|---------------|
| 4                   | 5             | 32            |
| 8                   | 5             | 47.4          |
| 15                  | 5             | 85.3          |
| 4                   | 10            | 31.2          |
| 8                   | 10            | 38.2          |
| 15                  | 10            | 55            |

O1. Minimal FiO<sub>s</sub>
***Fig O1**. Minimum FiO<sub>2</sub> in Phantom Pharynx vs. Oxygen Flow at CPAP pressures of 5 and 10 cm H<sub>2</sub>O.*

## Clinical Trial
### Objective
To evaluate the effective leakage of the ARM compared to current standard of care NIV masks in patients undergoing emergent CPAP or BiPAP treatment.

### Methods
Opportunistic randomized controlled trial.

After [HSREB approval at Western University](https://github.com/GliaX/Aerosol-Reducing-Mask/blob/master/ethics_application/2020-04-27%20Ethics%20Approval.pdf) participants determined to require non-invasive ventilation by attending MDs in the emergency departments of affiliated teaching hospitals were recruited and randomized to the ARM or control standard mask ([Fisher & Paykel RT043M non-vented mask with anti-asphyxiation valve](https://www.fphcare.com/en-ca/hospital/adult-respiratory/noninvasive-ventilation/rt043/)).

Patients requiring NIV for an actue indications were assessed for inclusion. Exclusion criteria were: Age <18 years; respiratory failure due to non-pulmonary pathology; impaired level of consciousness (Glasgow coma scale <10); upper gastrointestinal bleeding; Chest trauma; Agitatation or violence.

Patients were ventialted using a Resmed (San Diego, US) Stellar 150 Non-invasive ventilator. The device's internal leak logging system was used to document mask leak. Trial was continued until either NIV was no longer deemed medically indicated by the attending team to a maximum of 24 hours. Arterial or venous blood gases collected during routine care of the patient were monitored to ensure adequacy of ventilation.

Primary end-point was proportion of time under treatment with mask leak < 0.5 L/min (registering as 0 L/min by machine). Secondary end-points included ulceration score (National Advisory Panel on Pressure Ulcer Scale), mask fit (Likert-like 5 point scale, 1 = poor; 5 = excellent); and patient tolerance of the device (1 = poor; 5 = excellent).

Additional collected data included: demographics (age, sex); morphologic parameters (height, weight, presence of dentures, facial hair); metabolic data (arterial or venous blood gas); vital signs (temperature, pulse, respirations, blood pressure, oxygen saturation); Ventilation parameters (mode, IPAP, EPAP) and fit and comfort (mask fit evaluated by RT, and patient tolerance of mask).

## Results
The study was stopped after randomization of 16 patient (6 intervention, 10 control) due to results suggesting failure of the ARM to reduce leaks compared to the control device (Fig T1 & T2).

There were no major adverse events during the trial related to the device. 

T1. Mask Leak - Control

***Fig T1**. Distribution of mask leak flows for each patient with the control mask (N=10). 7/10 patients had leak of 0.5 L/min or less for at least half of the treatment duration*

T2. Mask Leak - ARM

***Fig T2**. Distribution of mask leak flows or each patient with the ARM (N=6). Only 2 of 6 patients had leaks of 0.5 L/min or less for more than half of the treatment duration*.

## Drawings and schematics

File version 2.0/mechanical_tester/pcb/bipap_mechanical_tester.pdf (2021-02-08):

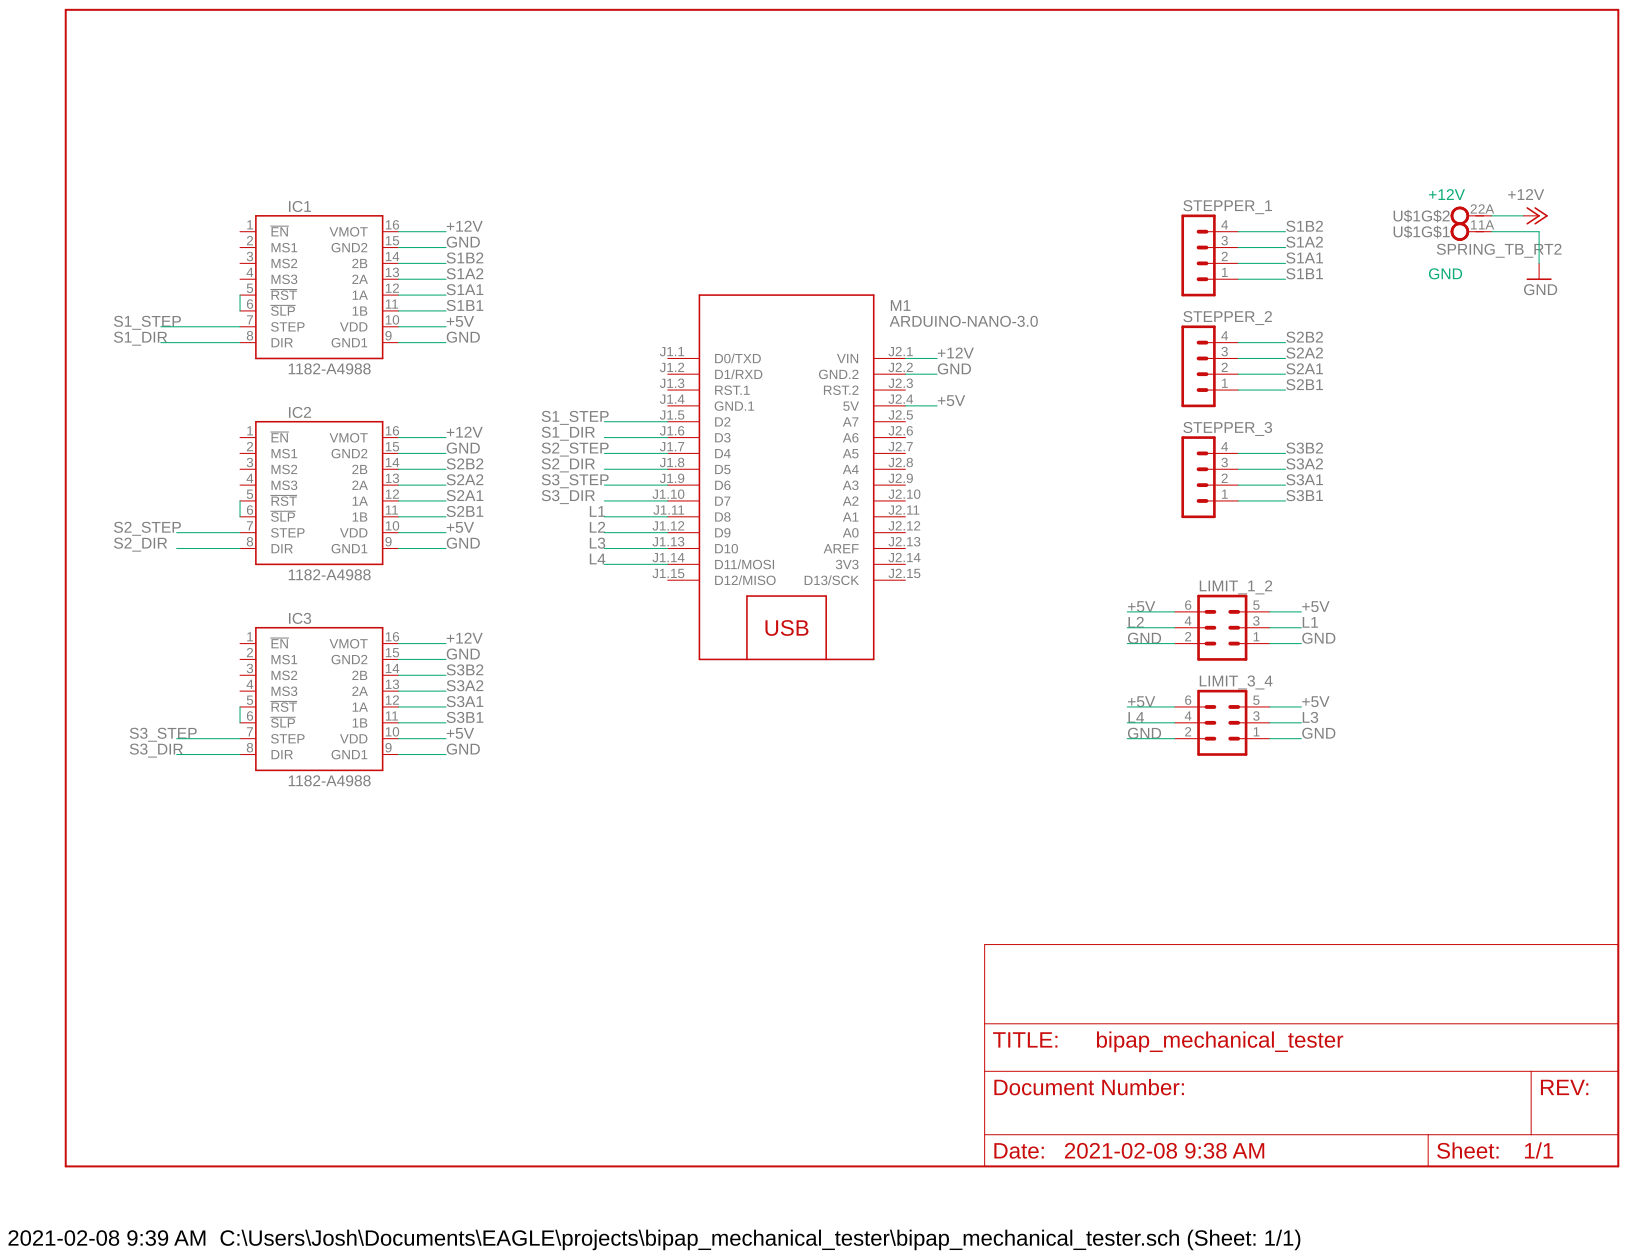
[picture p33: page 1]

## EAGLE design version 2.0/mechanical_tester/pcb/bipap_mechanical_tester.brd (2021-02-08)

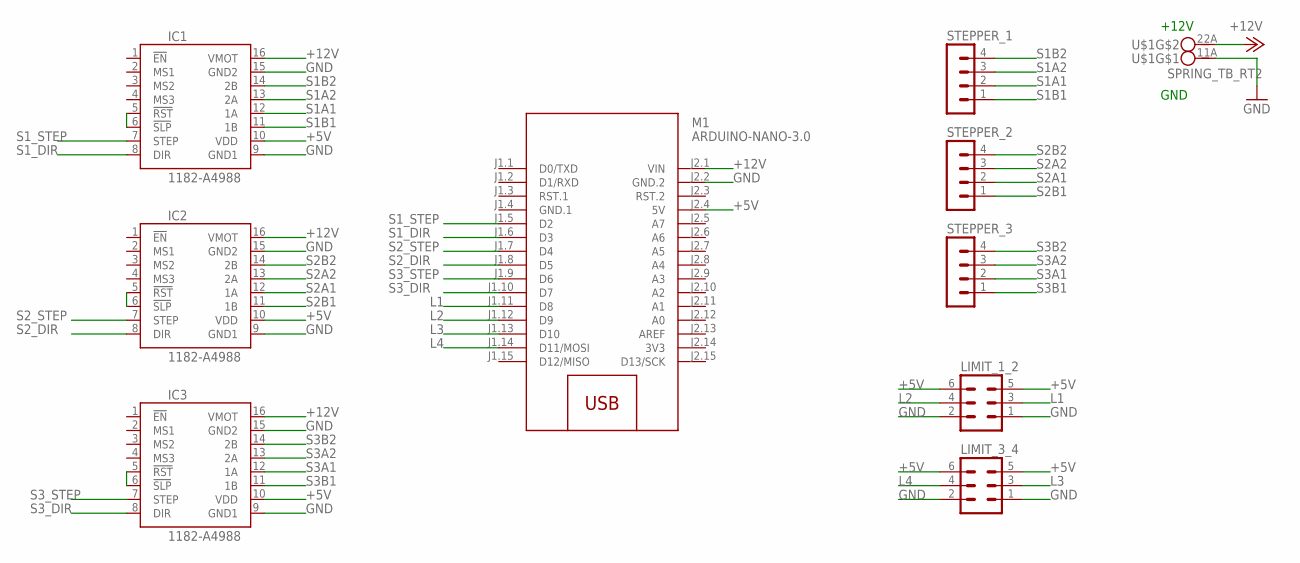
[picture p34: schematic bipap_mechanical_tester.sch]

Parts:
IC1, IC2, IC3: 1182-A4988; A4988
LIMIT_1_2, LIMIT_3_4: MA03-2
M1: ARDUINO-NANO-3.0
STEPPER_1, STEPPER_2, STEPPER_3: MA04-1
U$1: SPRING_TB_RT2

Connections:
3V3: M1.J2.14 (3V3)
+5V: IC1.10 (VDD), IC2.10 (VDD), IC3.10 (VDD), LIMIT_1_2.5, LIMIT_1_2.6, LIMIT_3_4.5, LIMIT_3_4.6, M1.J2.4 (5V)
+12V: IC1.16 (VMOT), IC2.16 (VMOT), IC3.16 (VMOT), M1.J2.1 (VIN), U$1.2A (2)
GND: IC1.9 (GND1), IC1.15 (GND2), IC2.9 (GND1), IC2.15 (GND2), IC3.9 (GND1), IC3.15 (GND2), LIMIT_1_2.1, LIMIT_1_2.2, LIMIT_3_4.1, LIMIT_3_4.2, M1.J2.2 (GND.2), U$1.1A (2)
GND.1: M1.J1.4 (GND.1)
L1: LIMIT_1_2.3, M1.J1.11 (D8)
L2: LIMIT_1_2.4, M1.J1.12 (D9)
L3: LIMIT_3_4.3, M1.J1.13 (D10)
L4: LIMIT_3_4.4, M1.J1.14 (D11/MOSI)
unnamed: IC1.5 (!RST), IC1.6 (!SLP)
unnamed: IC2.5 (!RST), IC2.6 (!SLP)
unnamed: IC3.5 (!RST), IC3.6 (!SLP)
S1A1: IC1.12 (1A), STEPPER_1.2
S1A2: IC1.13 (2A), STEPPER_1.3
S1B1: IC1.11 (1B), STEPPER_1.1
S1B2: IC1.14 (2B), STEPPER_1.4
S1_DIR: IC1.8 (DIR), M1.J1.6 (D3)
S1_STEP: IC1.7 (STEP), M1.J1.5 (D2)
S2A1: IC2.12 (1A), STEPPER_2.2
S2A2: IC2.13 (2A), STEPPER_2.3
S2B1: IC2.11 (1B), STEPPER_2.1
S2B2: IC2.14 (2B), STEPPER_2.4
S2_DIR: IC2.8 (DIR), M1.J1.8 (D5)
S2_STEP: IC2.7 (STEP), M1.J1.7 (D4)
S3A1: IC3.12 (1A), STEPPER_3.2
S3A2: IC3.13 (2A), STEPPER_3.3
S3B1: IC3.11 (1B), STEPPER_3.1
S3B2: IC3.14 (2B), STEPPER_3.4
S3_DIR: IC3.8 (DIR), M1.J1.10 (D7)
S3_STEP: IC3.7 (STEP), M1.J1.9 (D6)

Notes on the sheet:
+12V
GND

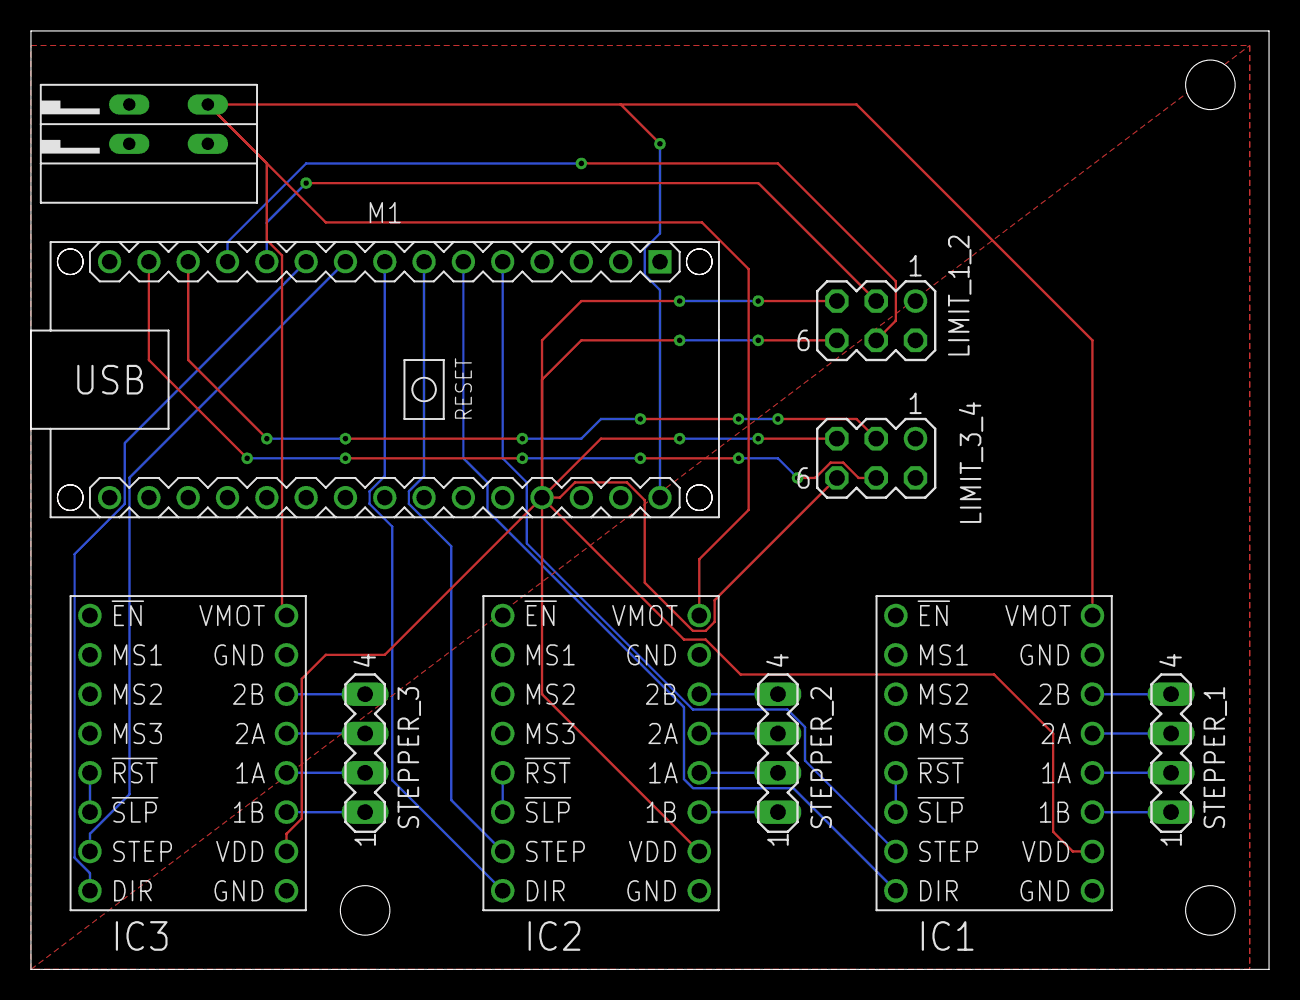
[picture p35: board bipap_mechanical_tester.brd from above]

Board: 2 copper layers, 80.0 x 60.6 mm, 10 parts (0 on the bottom side), 28 nets.

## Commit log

2020-04-13 Add Adapter v1.0 STL
    [adapter.stl]
2020-04-14 Add device label
2020-05-13 Adapter 3MF
    [adapter.3mf]
2020-05-15 Start quality assurance and add submersion testing
    [submersion_test_rig_bottom.scad, submersion_test_rig_bottom.stl, submersion_test_rig_common.scad, submersion_test_rig_top.scad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]
2020-05-15 Embiggened plate to provide more stability while gripping mesh
    [submersion_test_rig_bottom.scad, submersion_test_rig_bottom.stl, submersion_test_rig_top.scad, submersion_test_rig_top.stl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]
2020-05-15 Add gentle slope to top part so water doesn't stick there
    [submersion_test_rig_top.scad, submersion_test_rig_top.stl]
2020-05-15 Move slots further out for more stability
    [submersion_test_rig_bottom.stl, submersion_test_rig_top.stl, submersion_test_rig_variables.scad]
2020-06-05 Modified device label for FDA compliance
2020-11-11 Add strap instructions
2021-01-29 added model files for scuba adapters
    [bipap_expiratory_port.step, bipap_expiratory_port.stl, bipap_inspiratory_port.step, bipap_inspiratory_port.stl]
2021-01-29 added images for the v2.0 connectors
2021-02-02 added f3d/f3z files
    [bipap_expiratory_port v35.f3d]
2021-02-05 added gcode and 3mf file for printing an expiratory and inspiratory port
    [bipap_expiratory_port.3mf]
2021-02-08 added mechanical fatigue tester design and electronics
    [4037N131_PLASTIC WORM GEAR.step, 4037N131_pinion.stl, 4in_cut_guide.stl, 57545K646_METAL WORM GEAR.step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]
2021-02-08 removed mechanical tester concept 1
    [body_1.stl, body_2.stl, body_3.stl, pinion.stl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]
2021-03-01 new version of expiratory port with larger lever arm for release
    [bipap_expiratory_port v35.f3d, bipap_expiratory_port v43.f3d, bipap_expiratory_port v43.step, bipap_expiratory_port.3mf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]
2021-04-29 added more material to expiratory port tabs and reduced height of expiratory port lever
    [bipap_expiratory_port v43.f3d, bipap_expiratory_port v43.step, bipap_expiratory_port v47.f3d, bipap_expiratory_port v47.step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]

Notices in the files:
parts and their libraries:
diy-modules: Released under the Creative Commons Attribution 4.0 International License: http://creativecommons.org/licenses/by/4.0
